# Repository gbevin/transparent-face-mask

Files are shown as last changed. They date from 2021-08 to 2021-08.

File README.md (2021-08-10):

# Transparent Reusable Face Mask

Vacuum formed and 3D printed transparent face mask with replaceable filters and an excellent seal.

I've made and donated over 1000 opaque 3D printed masks that have been fit-tested and and particle tested with great results. Using the same shape and fundamental design, I spent 4 months designing a transparent mask that fits better, has more airflow and better filtration.

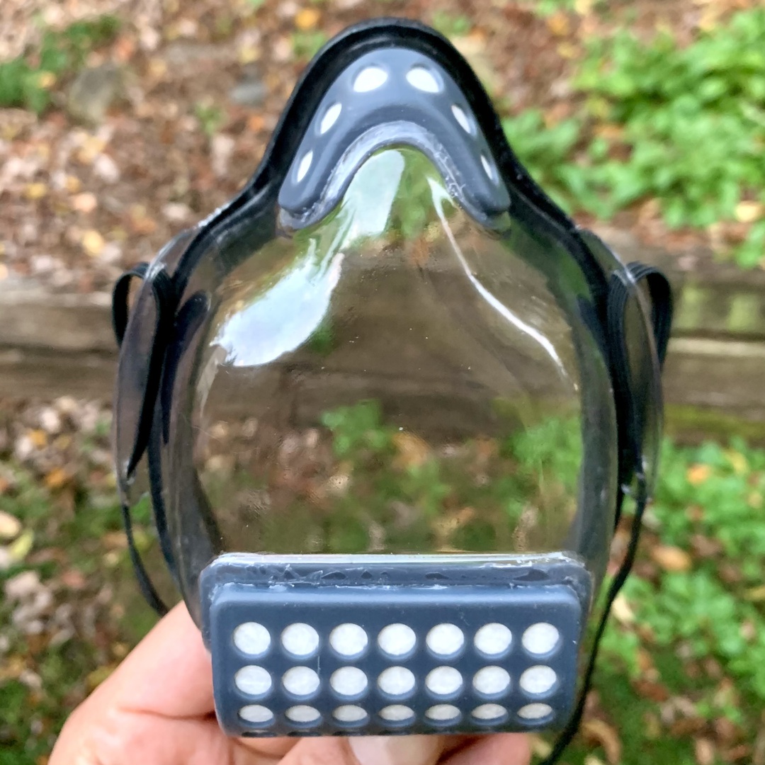
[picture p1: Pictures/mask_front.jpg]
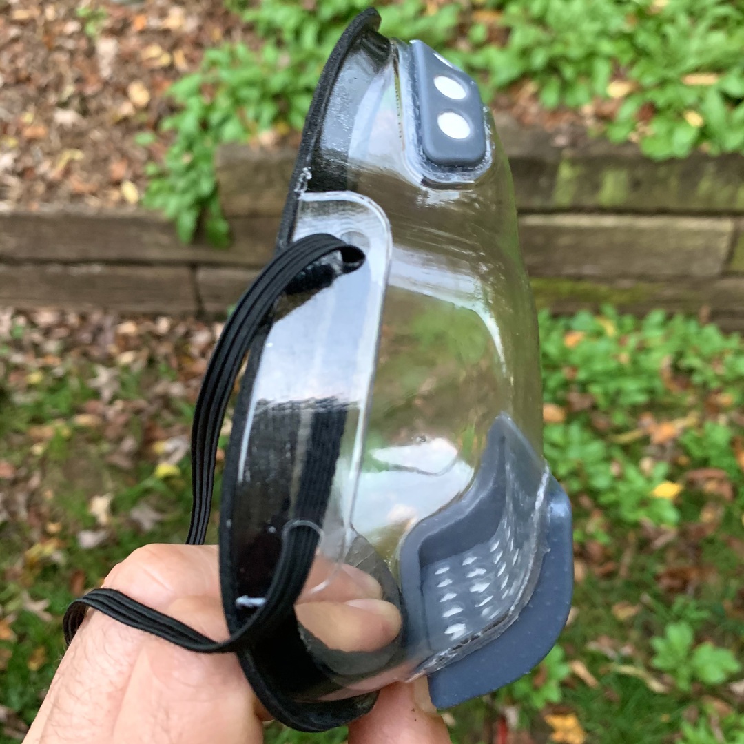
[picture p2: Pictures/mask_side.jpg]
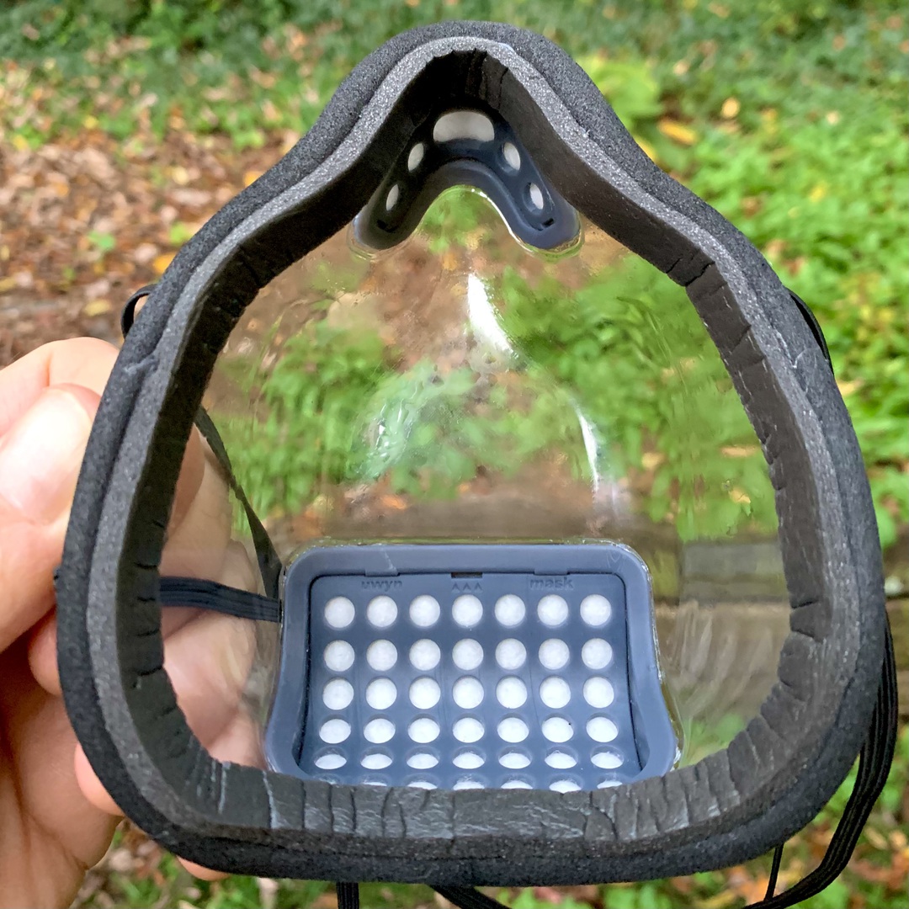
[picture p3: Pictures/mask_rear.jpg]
  

Created by Geert Bevin.

This work is freely distributed under the CC BY-SA 4.0 License.

If you want to support my efforts, please consider donating through:
http://paypal.me/geertbevin

## Design

The design was made with Moment of Inspiration: http://moi3d.com

You'll find the `3dm` files in the `Design` folder.

## Build Instructions

Detailed instructions on how to build this mask is available in the [included howto](https://htmlpreview.github.io/?https://github.com/gbevin/transparent-face-mask/blob/master/Instructions/howto.html).

## Features

* works with FaceID, might require setup of alternate appearance
* excellent smile and lip-reading visibility
* great airflow through natural vertical convection (top and bottom openings)
* replaceable filters that can be cut from any flat filter material (shape templates included)
* can be treated with temporary anti-fog spray
* edge is lined with soft weather-sealing foam to create an excellent seal
* flexible but rigid mask shell allows for comfortable facial muscle movements

## Sizing

For masks sizing: measure down from the bridge of the nose to the bottom of the chin. Don't follow the curve, make sure to measure in a straight line, see photo.

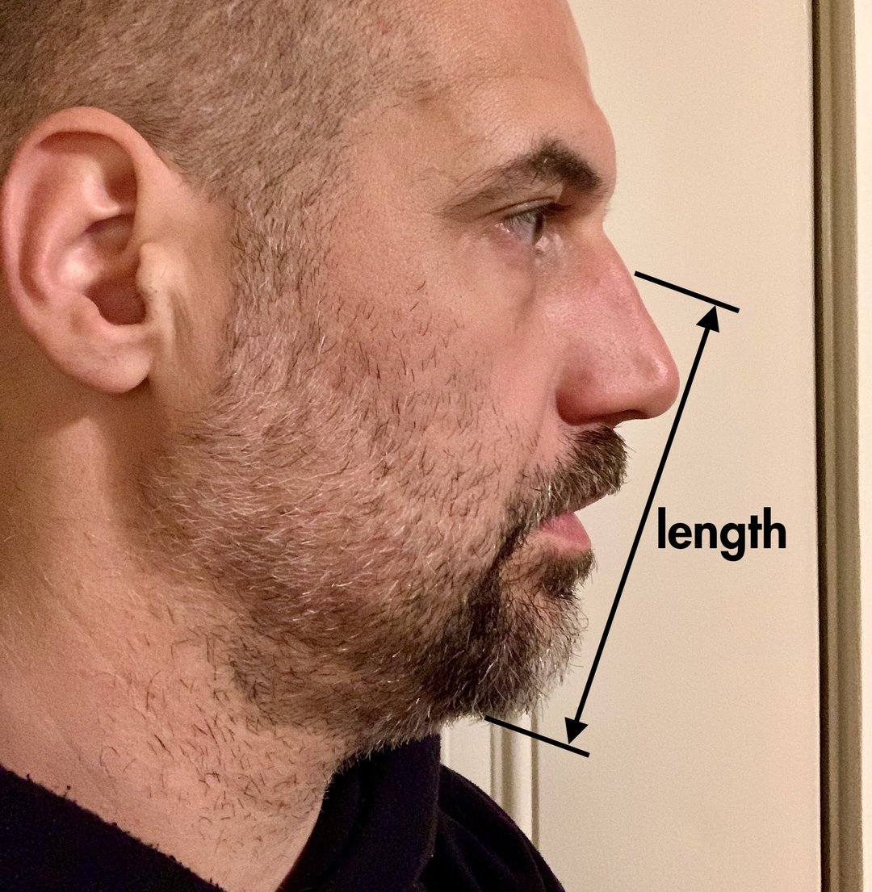
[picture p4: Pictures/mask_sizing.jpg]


This is how the sizes relate to the measured length:
* XL : length >= 5"
* L : length 4.5"-5"
* M : length < 4.5"

## Filters

It's recommended to daily replace the filters when in constant use.
For occasional use, weekly replacement is acceptable.

Recommended filter materials are:
* Filti : https://filti.com/product/filti-face-mask-material/
* BioDefensor: https://biodefensor.com

## Anti-fog

Anti-fog spray should be applied by using a microfibre cloth, spraying the cloth in order to not wet the mask's filters, then gently pat (not wipe) the inside of the mask with the humidified part of the cloth. Let dry overnight.

Recommended anti-fog products:
* Rain-X : https://www.rainx.com/product/glass-water-repellents-cleaners/rainx-anti-fog

Outside use of the mask in cold temperatures will cause condensation and reduced transparency.

## Disclaimer

**NO GUARANTEES:** This mask is not approved as N95 replacements and is not guaranteed to help against COVID-19 or any other disease. I have however done extensive research and the model I provide is the best I can create with my available tools and supplies.

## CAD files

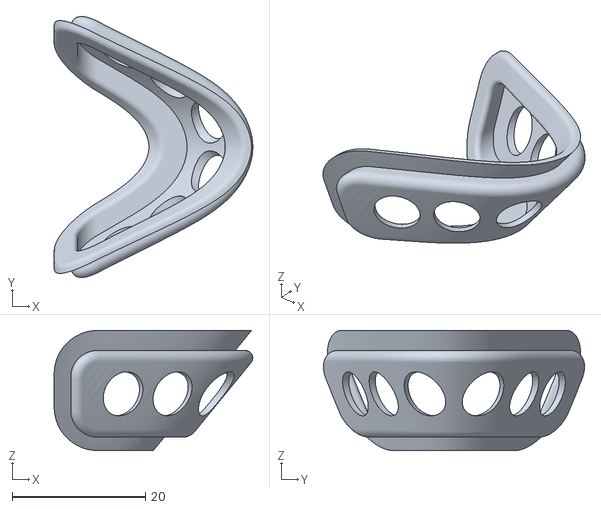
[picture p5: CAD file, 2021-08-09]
STL/large_top_insert.stl
29.8 x 39.1 x 18.0

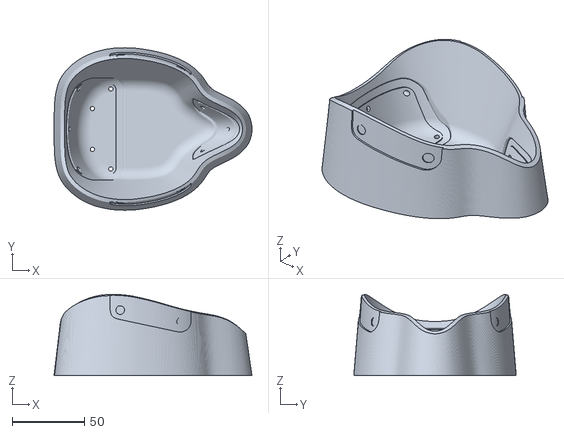
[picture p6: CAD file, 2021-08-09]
STL/large_shell_mold.stl
137.4 x 112.8 x 56.4

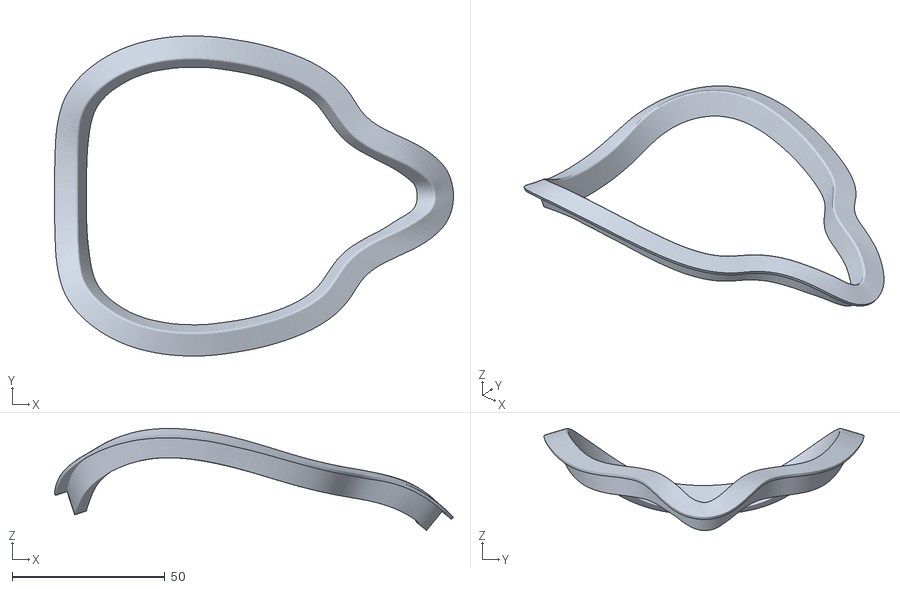
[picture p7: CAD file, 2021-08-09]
STL/large_seal.stl
130.7 x 104.8 x 33.4

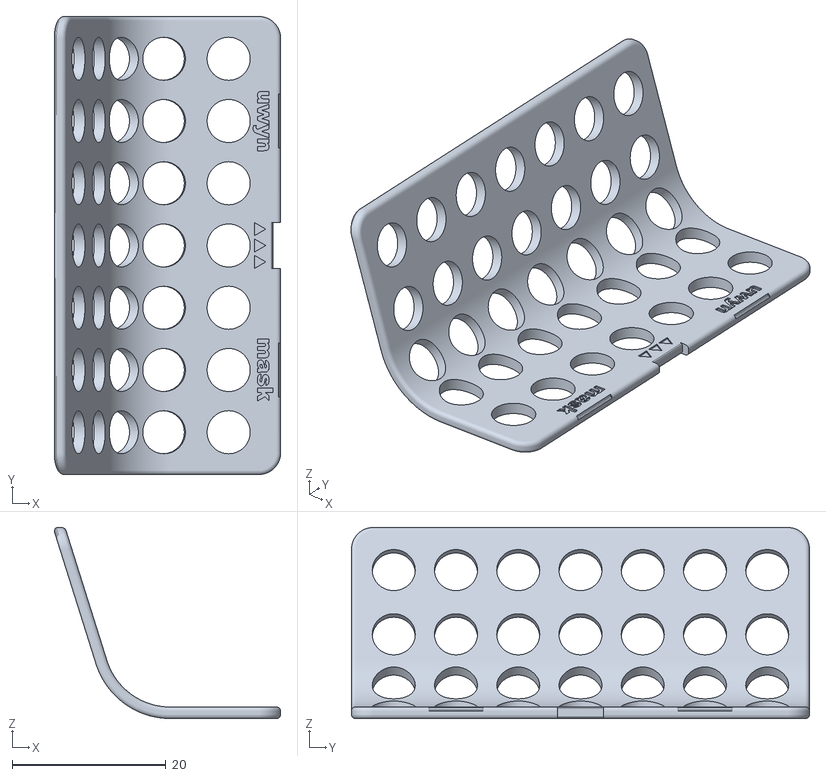
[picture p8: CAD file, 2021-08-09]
STL/medium_bottom_grate.stl
29.5 x 59.6 x 24.9

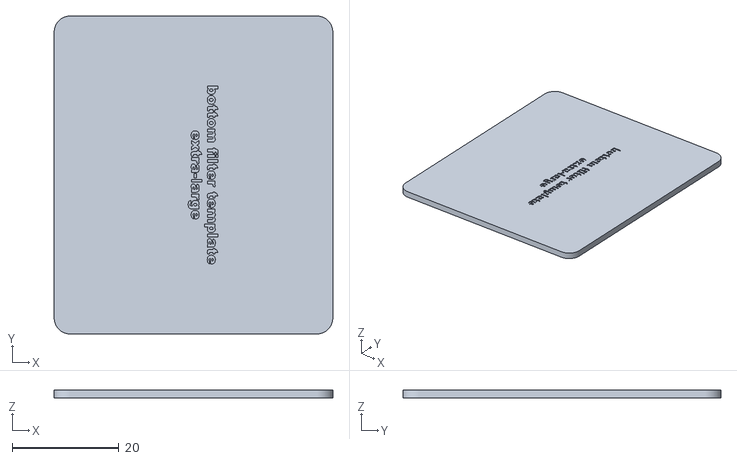
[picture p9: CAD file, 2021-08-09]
STL/extralarge_template_bottom.stl
52.2 x 59.6 x 1.50

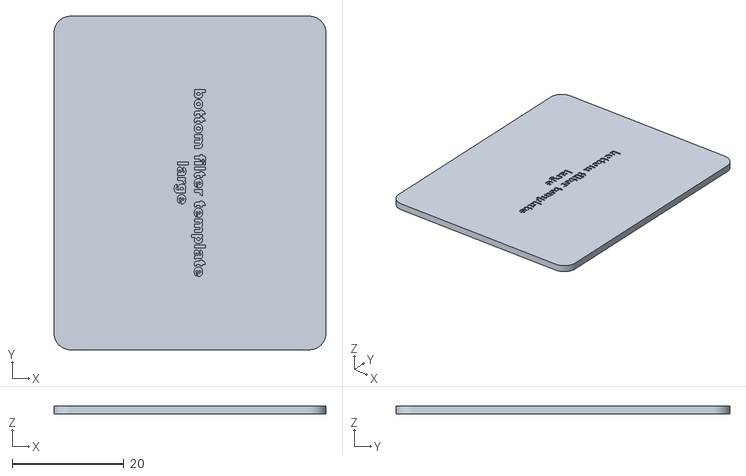
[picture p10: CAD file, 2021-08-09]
STL/large_template_bottom.stl
48.6 x 59.6 x 1.50

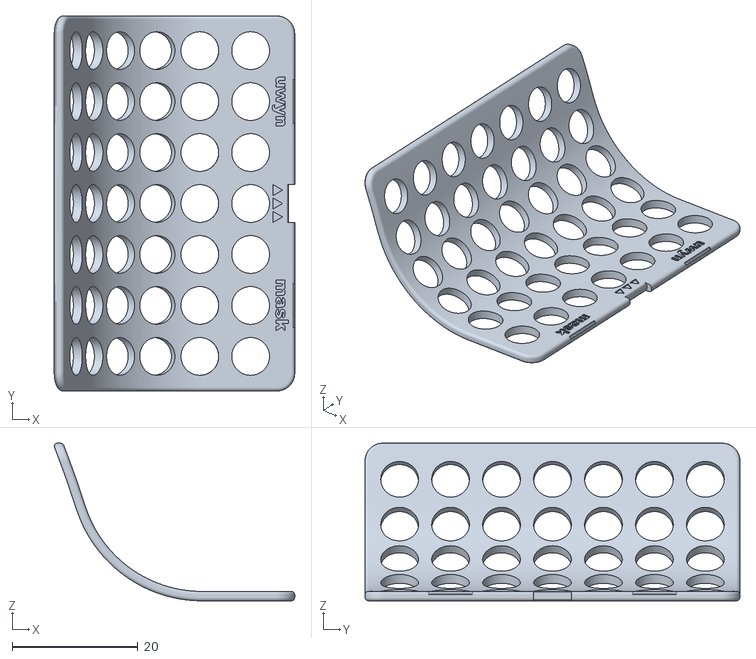
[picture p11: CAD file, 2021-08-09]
STL/extralarge_bottom_grate.stl
38.2 x 59.6 x 25.1

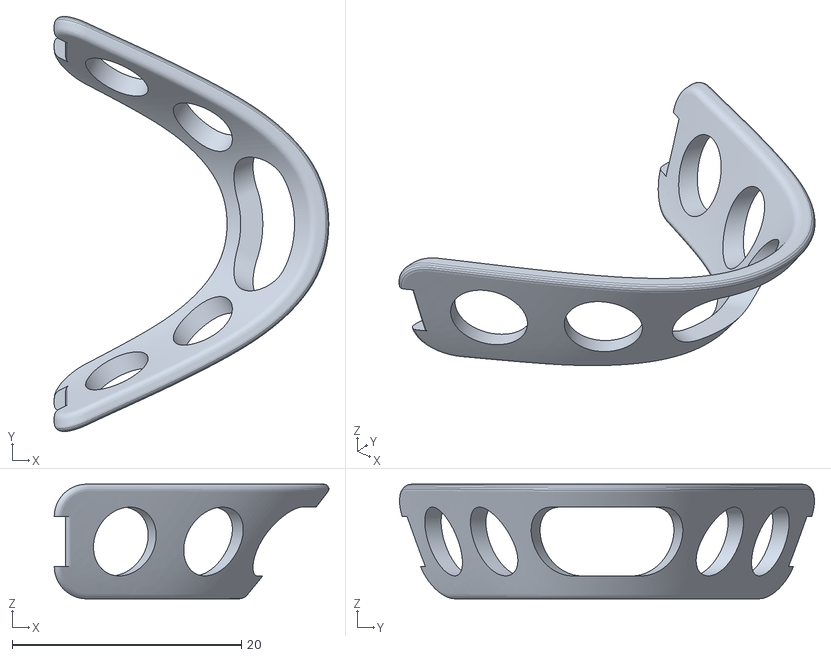
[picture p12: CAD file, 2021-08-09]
STL/extralarge_top_grate.stl
24.0 x 36.2 x 10.0

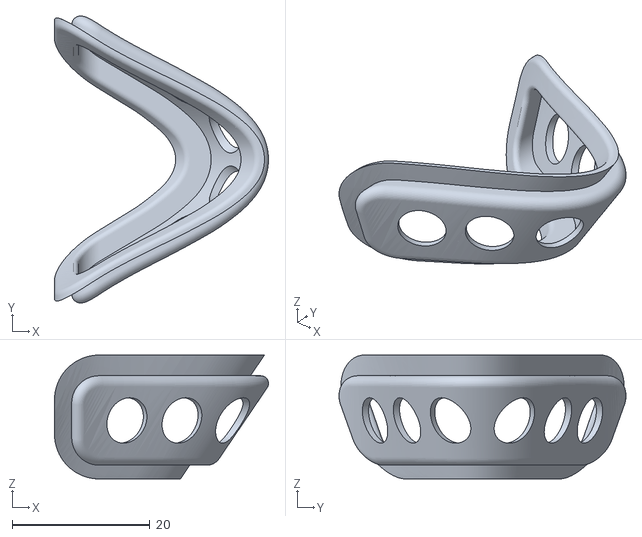
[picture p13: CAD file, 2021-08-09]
STL/medium_top_insert.stl
31.1 x 41.7 x 18.0

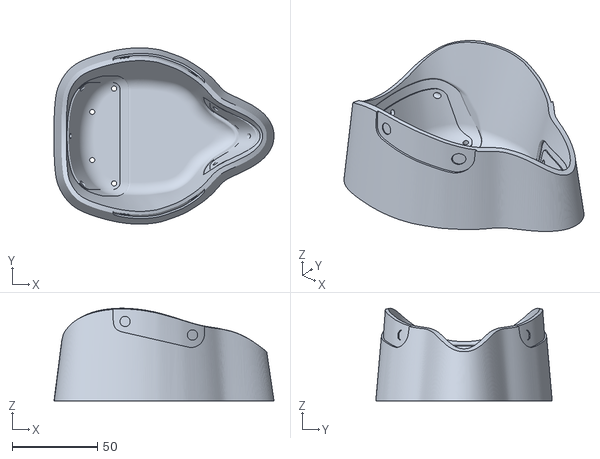
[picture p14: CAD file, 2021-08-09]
STL/medium_shell_mold.stl
129.1 x 103.5 x 54.3

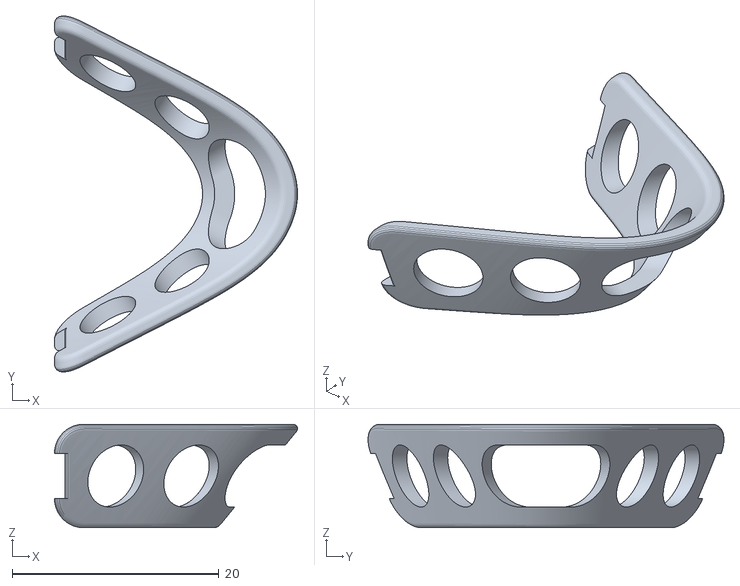
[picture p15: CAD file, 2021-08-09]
STL/large_top_grate.stl
23.5 x 34.4 x 10.0

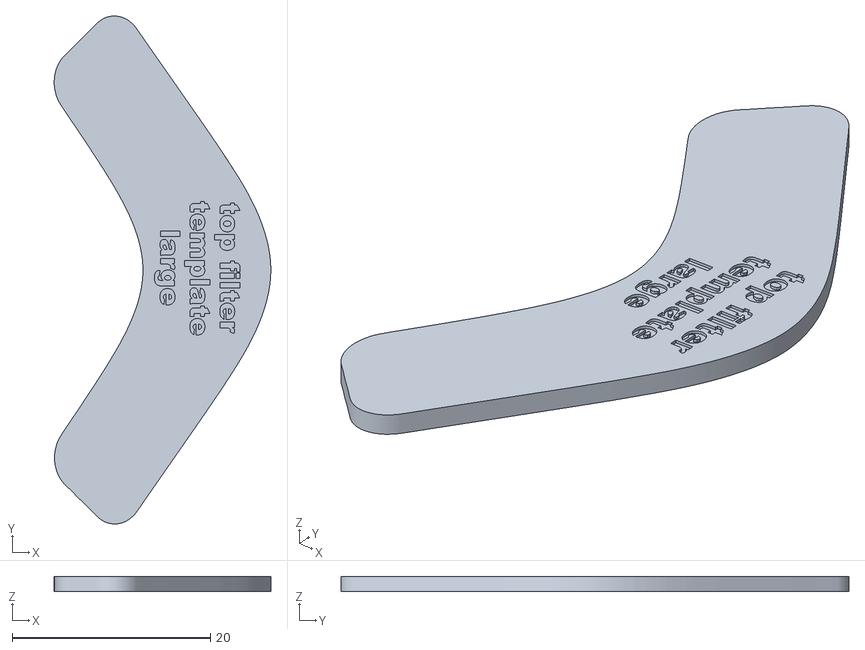
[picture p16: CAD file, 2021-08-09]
STL/large_template_top.stl
21.9 x 51.3 x 1.50

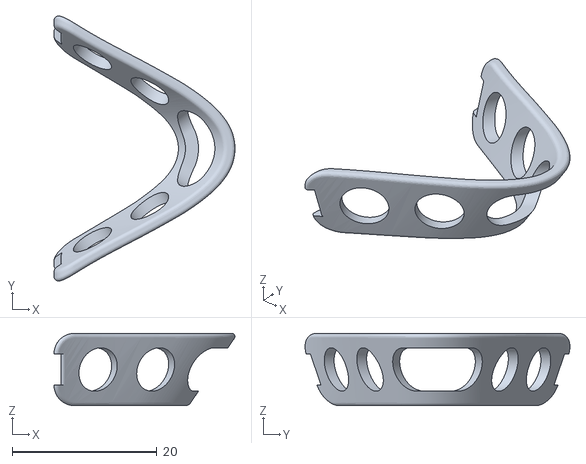
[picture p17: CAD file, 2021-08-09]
STL/medium_top_grate.stl
25.0 x 36.6 x 10.0

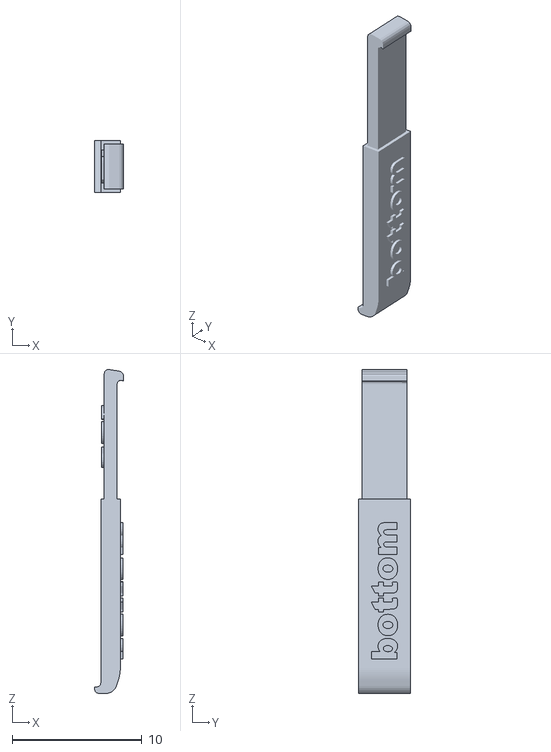
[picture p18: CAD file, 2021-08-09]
STL/large_grate_pull.stl
2.25 x 4.00 x 25.0

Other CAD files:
STL/medium_bottom_insert.stl
STL/extralarge_grate_pull.stl
STL/extralarge_seal.stl
STL/large_bottom_insert.stl
STL/extralarge_bottom_insert.stl
STL/extralarge_template_top.stl
STL/extralarge_top_insert.stl
STL/large_bottom_grate.stl
STL/medium_grate_pull.stl
STL/medium_seal.stl
STL/medium_template_bottom.stl
STL/medium_template_top.stl

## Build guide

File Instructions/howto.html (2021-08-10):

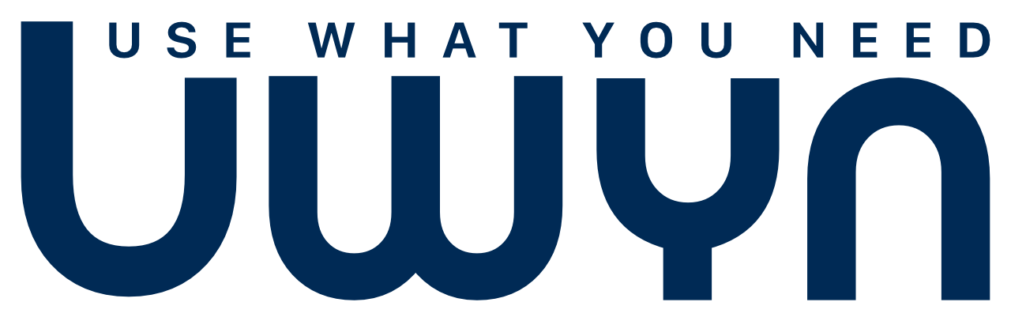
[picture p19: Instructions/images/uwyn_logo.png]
Uwyn logo
 (http://uwyn.com)

Transparent Reusable Face Mask
Build Instructions

# Introduction

During the 2020 COVID-19 pandemic, I have made and donated over 1000 opaque 3D printed masks that have been fit-tested and particle tested with great results. Using the same basic shape and fundamental design, I spent four months designing a transparent mask that fits better, has more airflow and better filtration.

  

## Feature Overview

- works with FaceID, might require setup of alternate appearance
- excellent smile and lip-reading visibility
- great airflow through natural vertical convection (top and bottom openings)
- replaceable filters that can be cut from any flat filter material (shape templates included)
- can be treated with temporary anti-fog spray
- edge is lined with soft weather-sealing foam to create an excellent seal
- flexible but rigid mask shell allows for comfortable facial muscle movements

NO GUARANTEES: This mask is not approved as N95 replacement and is not guaranteed to help against COVID-19 or any other disease.

These instructions will step you through how to make these transparent masks using the tools and equipment that are at my disposal. I've provided the design files and STL exports for you to be able to adapt these instructions to your own environment.

The latest version of these files is freely available under the CC BY-SA 4.0 License from here:
https://github.com/gbevin/transparent-face-mask

# Create the Mask Mold

The shell of the mask is designed to be transparent, light, flexible, scratch and shock resistant. The most viable small scale production technology to achieve this, turned out to be vacuum forming. This heats a sheet of clear PETG plastic and pulls it over a mold by creating a vacuum. Here, this mold is 3D printed and polished in order to achieve the highest possible clarity.

The heat of vacuum forming requires molds to be heat resistant, which needs to be taken into account when selecting the 3D printing technology and material used. Having FDM and MSLA printers available, FDM with polycarbonate filament was the best choice at my disposal. For these molds, I'm using a Raise3D E2 (https://www.raise3d.com/e2/) printer and Polymaker PolyMax PC (https://us.polymaker.com/product/polymax-pc/) filament.

The print settings are:

- Nozzle: 0.4mm
- Layer: 0.1mm
- Walls: 3
- Infill: 30% Gyroid
- Extruder temperature: 270°C
- Bed temperature: 100°C

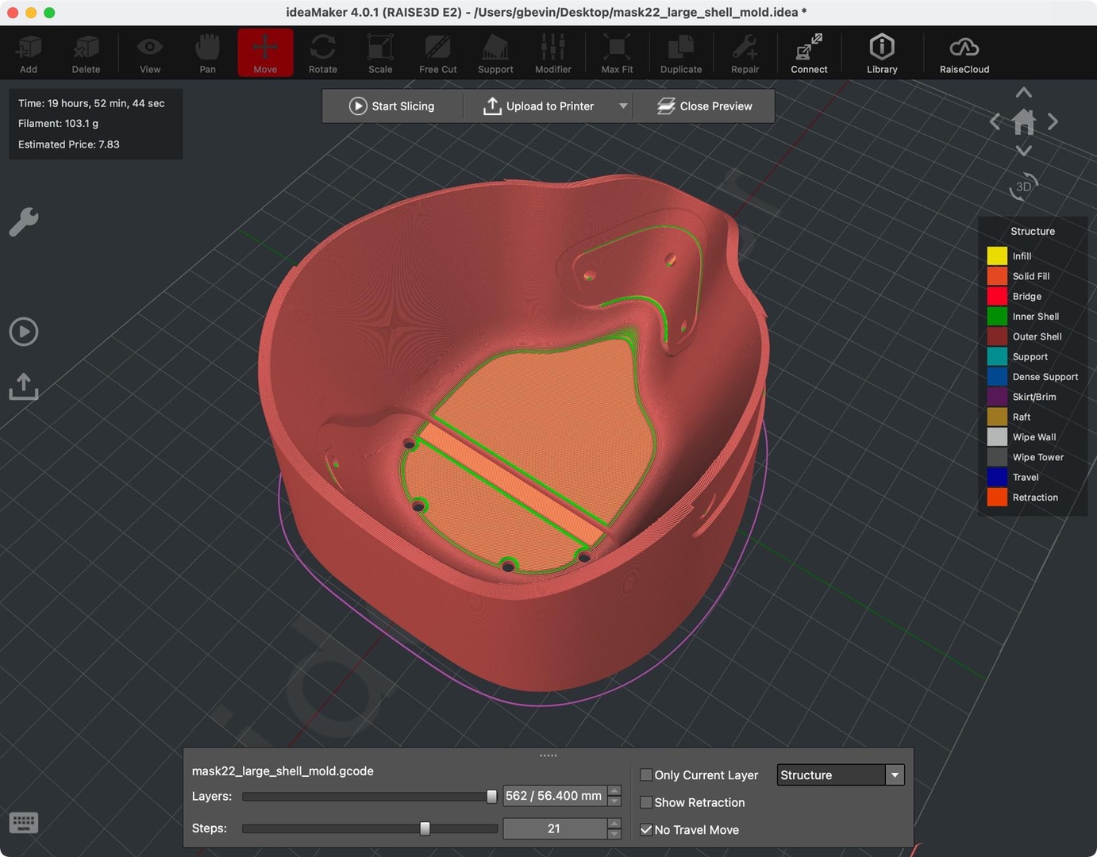
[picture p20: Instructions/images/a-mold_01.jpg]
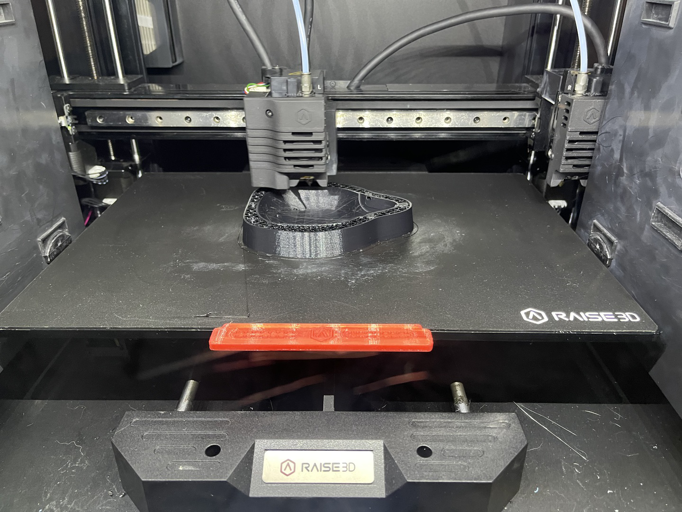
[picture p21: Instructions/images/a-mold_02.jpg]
 

Once the mold has finished printing, it's important to sand and polish it to the finest smoothness possible because vacuum forming will transfer even the smallest imperfection to the plastic that's pulled over the mold.

Finishing the mold is a very labor intensive process as you manually go through a series of sand paper grits. I'm using the following in order: 80, 150, 220, 320, 400, 800, 1000, and 3000. Don't press too hard because there is a risk of separating filament layers and creating unintended holes as they come loose during sanding. You can achieve a very smooth finish by using Brasso as the last step with a microfiber cloth.

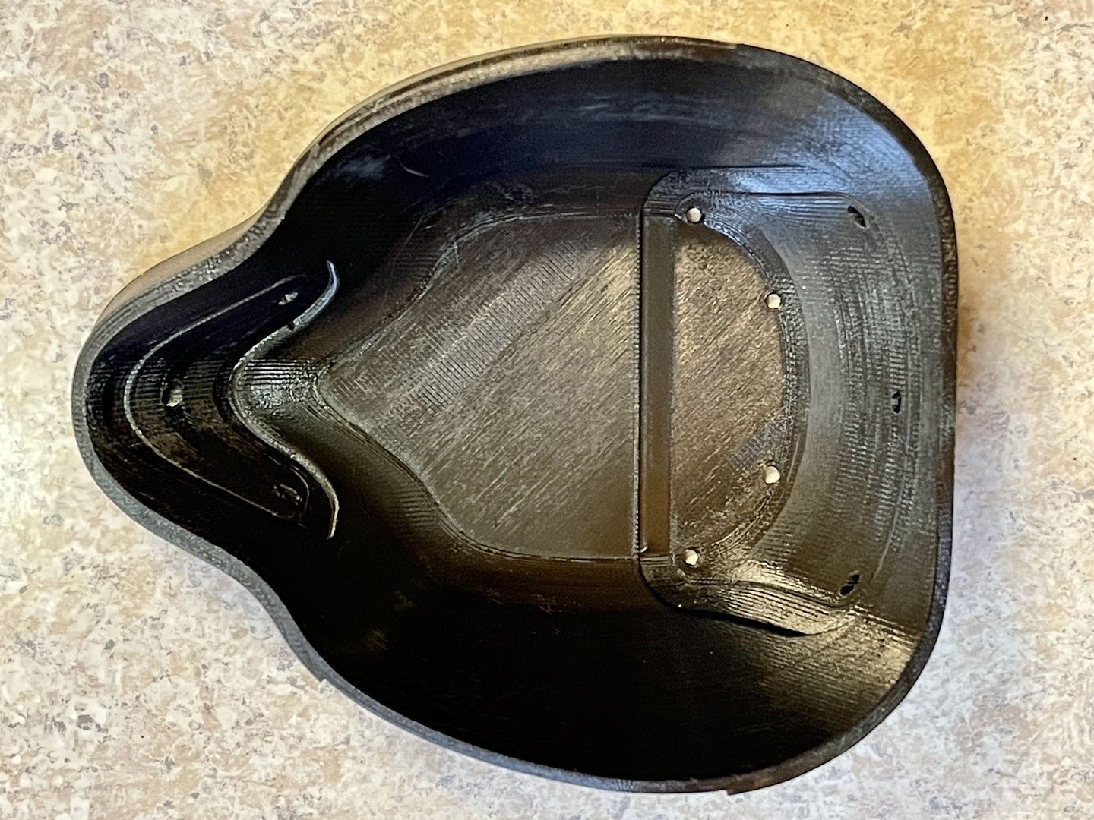
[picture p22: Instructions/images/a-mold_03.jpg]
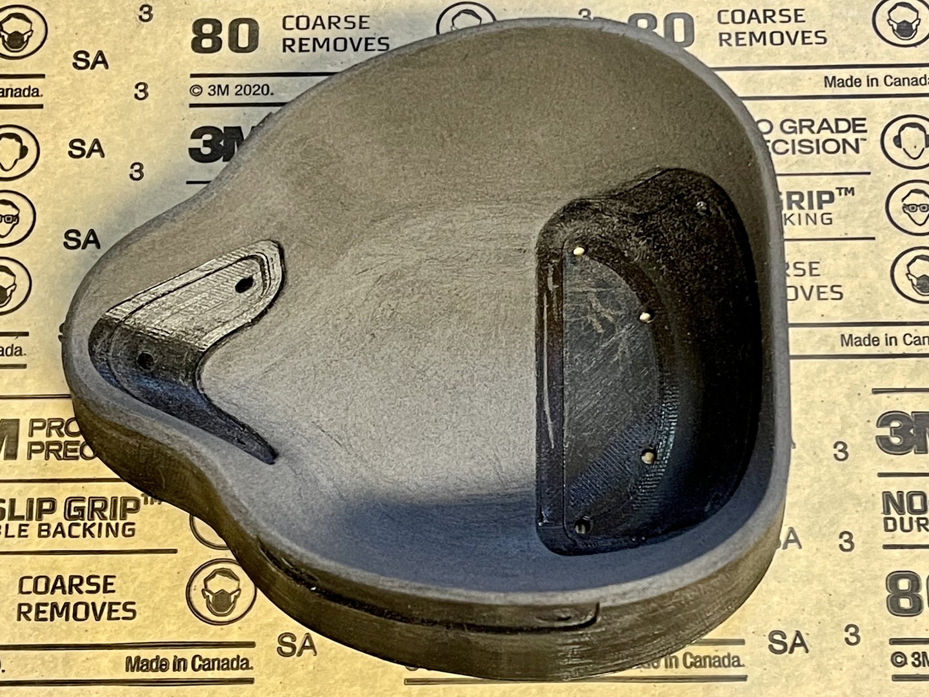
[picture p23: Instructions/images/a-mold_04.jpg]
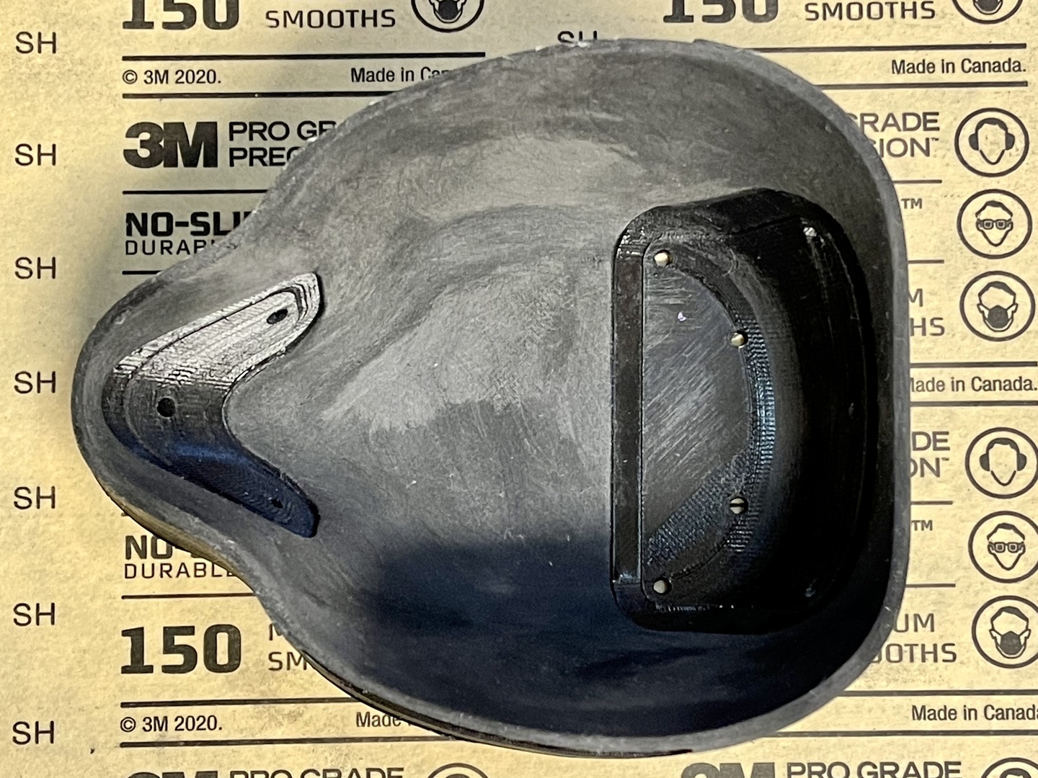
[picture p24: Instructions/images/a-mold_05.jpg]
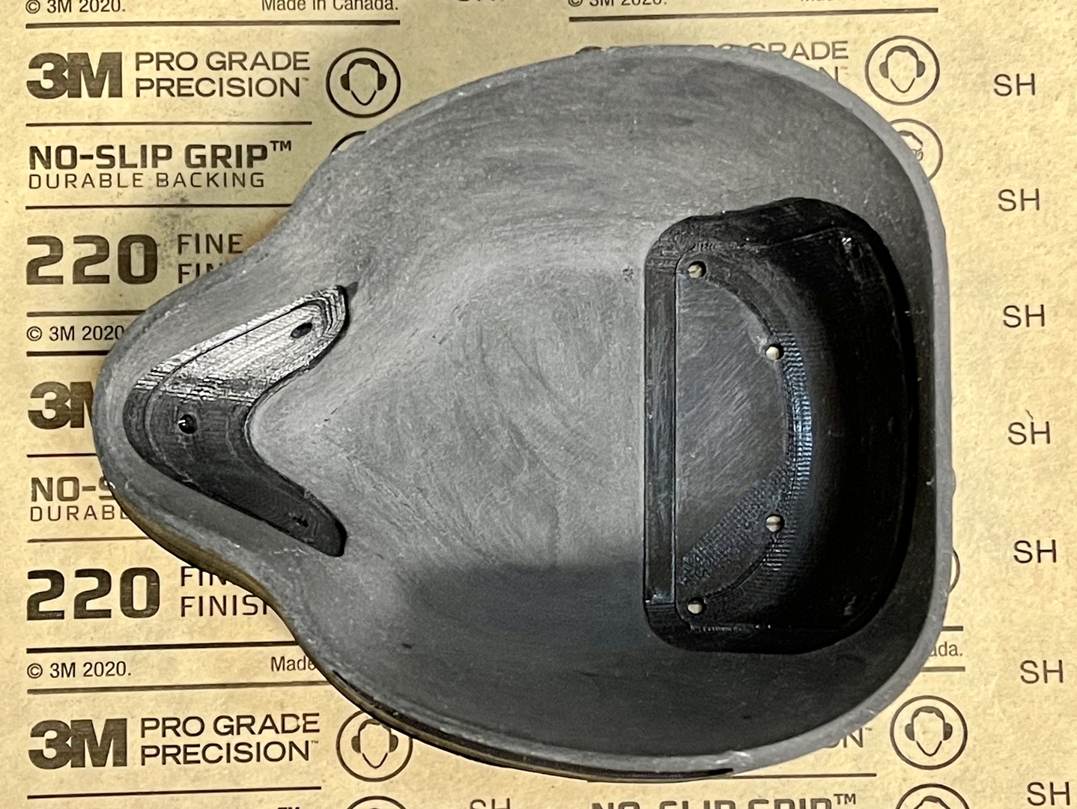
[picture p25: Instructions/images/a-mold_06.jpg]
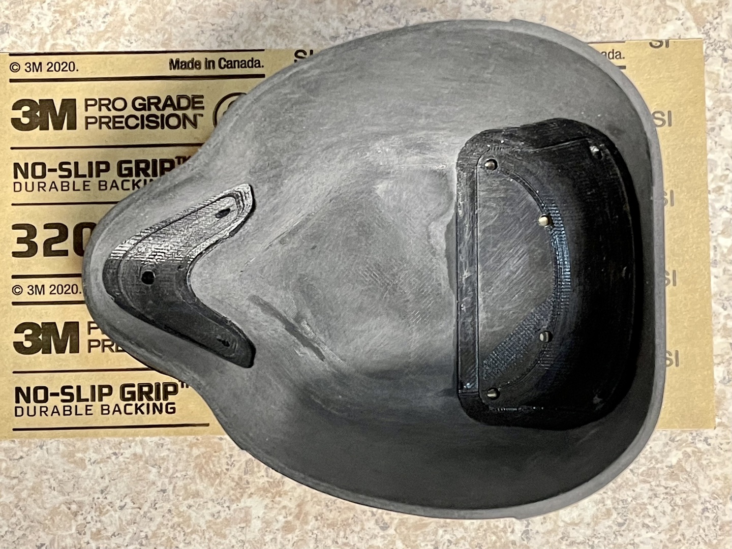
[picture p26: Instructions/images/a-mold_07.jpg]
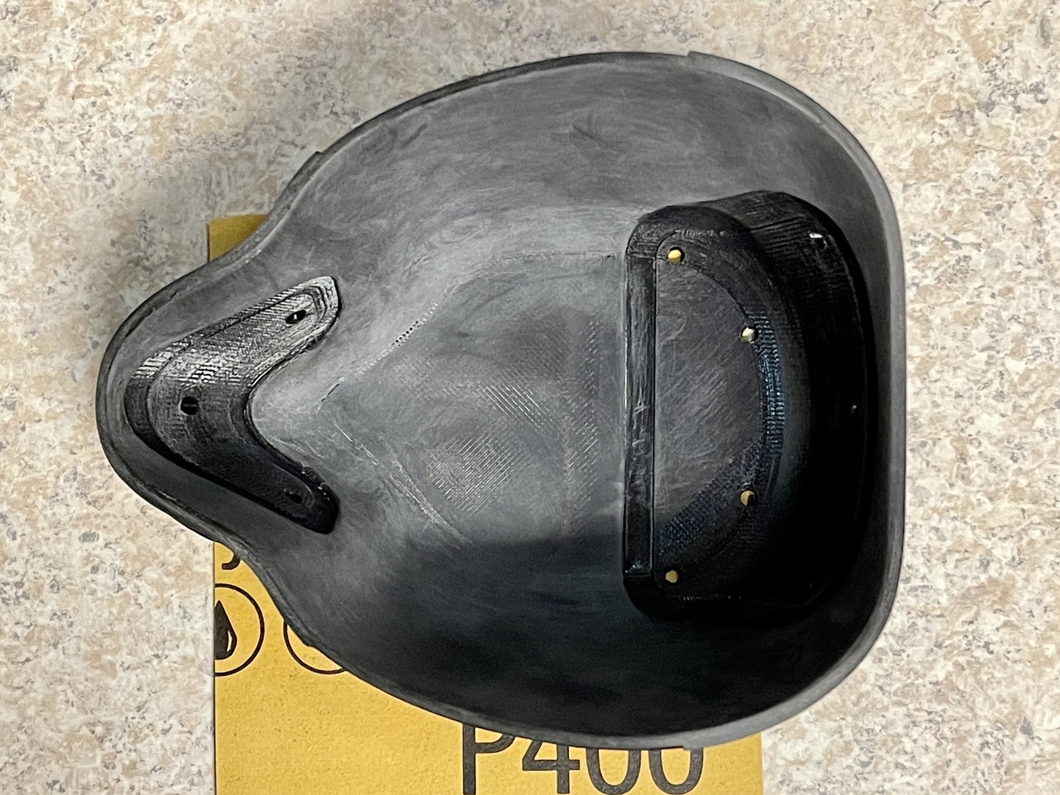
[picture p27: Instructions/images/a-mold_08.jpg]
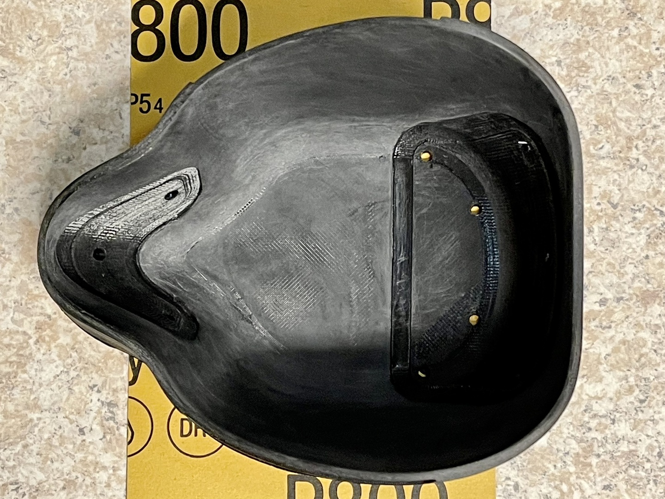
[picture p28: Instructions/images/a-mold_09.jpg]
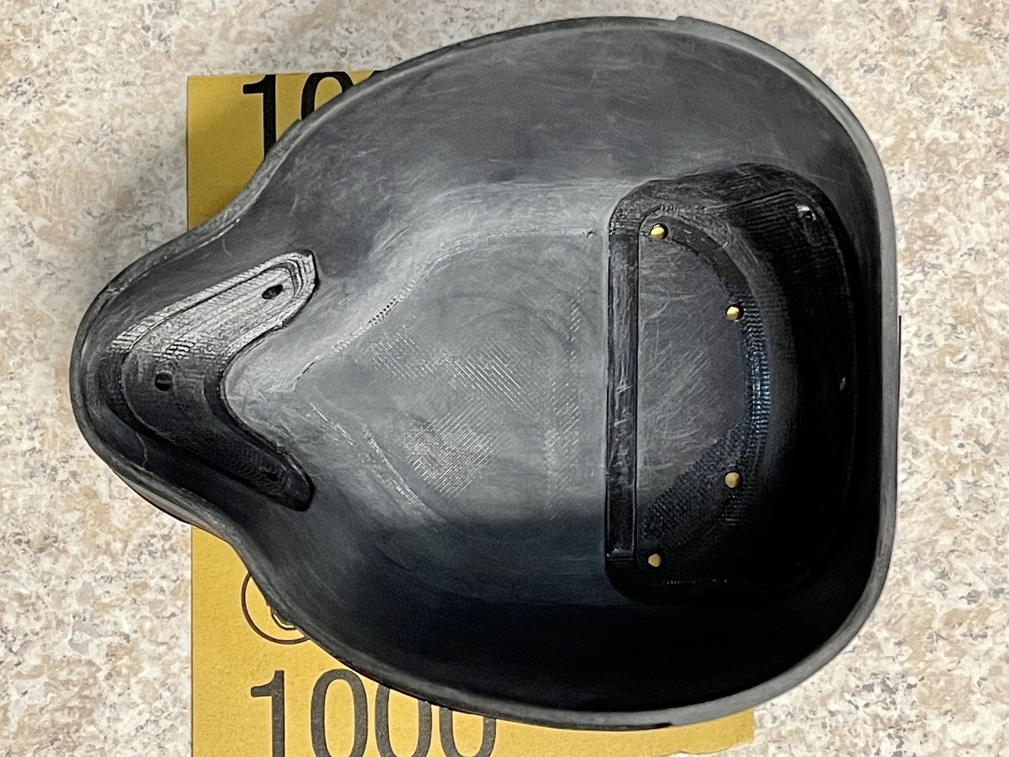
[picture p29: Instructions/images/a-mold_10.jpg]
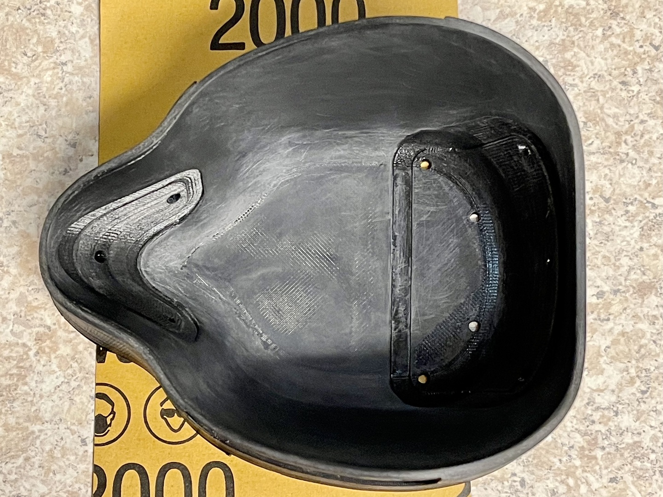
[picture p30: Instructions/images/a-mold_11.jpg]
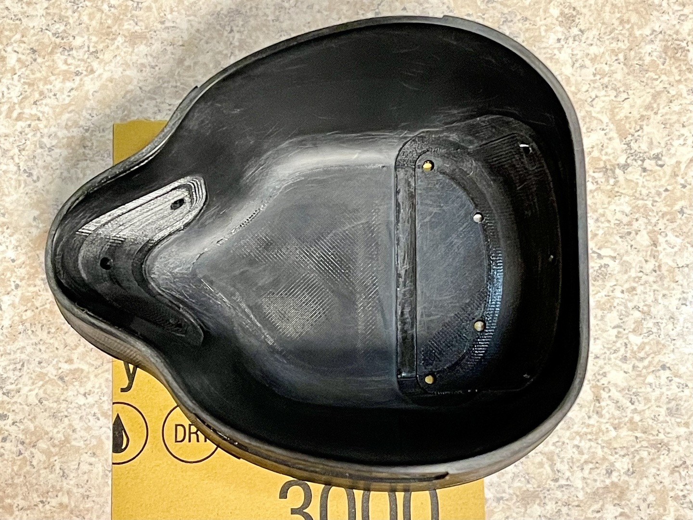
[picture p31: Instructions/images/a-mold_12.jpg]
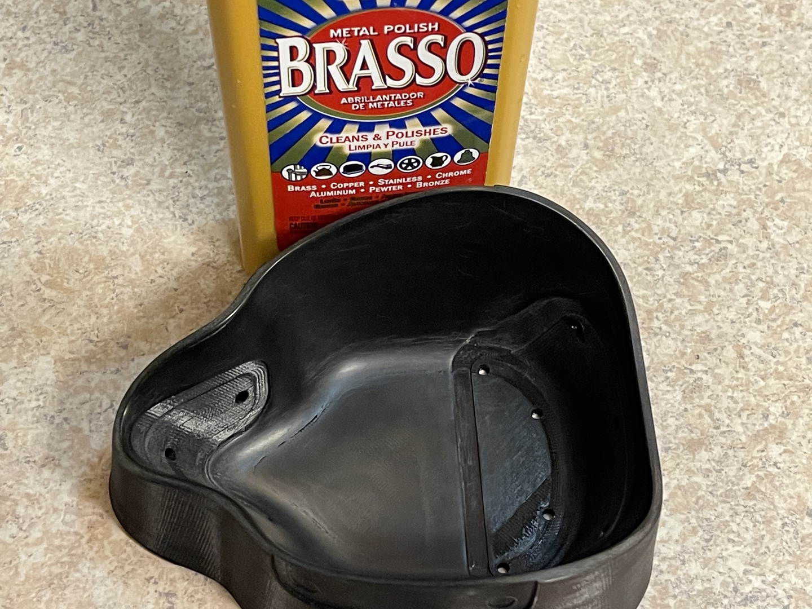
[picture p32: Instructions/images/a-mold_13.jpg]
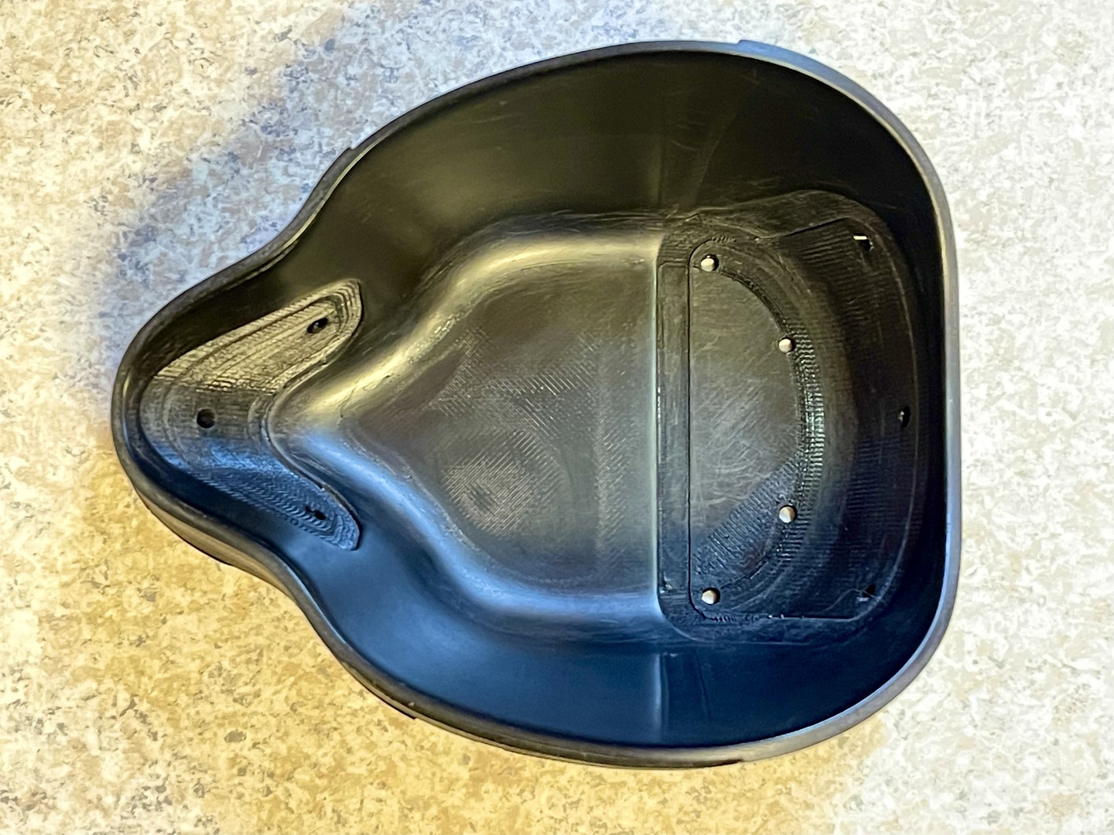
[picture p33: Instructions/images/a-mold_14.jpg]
           

# 3D Print the Mask Inserts

Inserts will be glued into the transparent shell in order to provide rigidity, to hold the replaceable filters and to prevent any air from entering or leaving the mask without having gone through filter material. These inserts can be printed with MSLA printers with minimal supports and when using a suitable resin, still provide enough strength and rigidity for daily use. I'm using an Epax3D X1K 6" Mono Printer (https://epax3d.com/collections/x-series-1/products/epax-x1k-mono-lcd-3d-printer) with the Epax3D Hard and Tough Resin (https://epax3d.com/collections/epax-resins/products/epax-abs-like-resin-gray) to which I've added additional black UV pigment (https://www.3dresinsolutions.com/products/cmykw-pigment-set) to create a darker shade of gray.

Once you've finished printing the inserts, grates, filter templates and little crowbar, remove the supports and thoroughly wash the items in 99% isopropyl alcohol. You'll have to keep your washing liquid fairly clean in order to prevent any residue from accumulating on the surfaces.

Make sure to wear appropriate PPE yourself when handling resin, especially heavy duty nitrile gloves (https://www.amazon.com/dp/B0192K9T78/ref=cm_sw_em_r_mt_dp_1HTX1VTY6T1CM7PHTT3E).

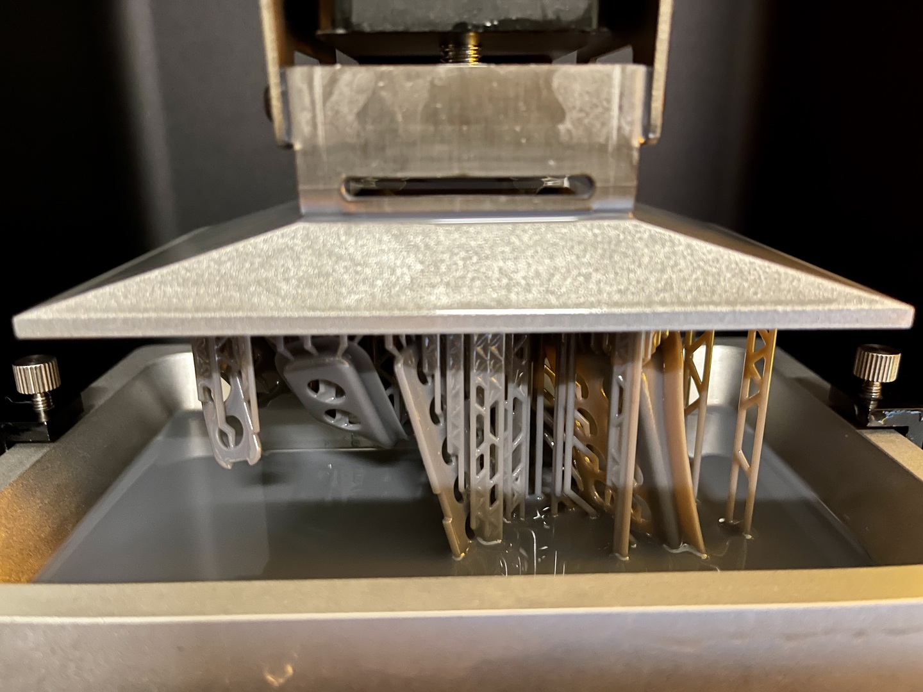
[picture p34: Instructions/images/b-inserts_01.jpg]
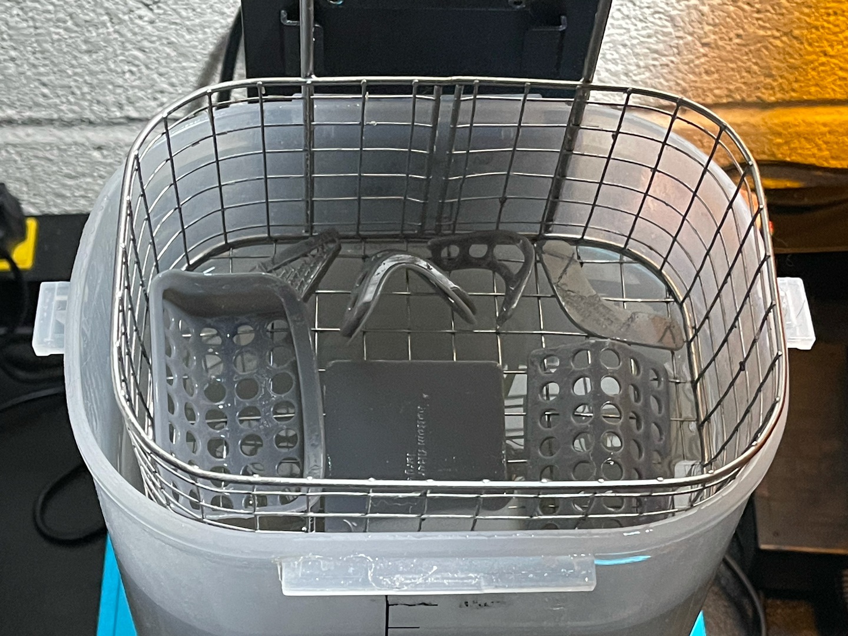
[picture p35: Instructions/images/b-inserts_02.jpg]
 

Let the items dry for at least 30 minutes when you remove them from the washing liquid. Afterwards you should finish the curing of the resin by exposing the items to a strong UV light for a sufficient amount of time. For both the washing and the curing, I use an AnyCubic Wash & Cure (https://www.anycubic.com/products/anycubic-washing-curing-machine) machine.

I cure the items in this device for at least 4 minutes, then turn the items over and put them in for another 4 minutes. Since uncured resin is toxic, you should be absolutely certain that all resin is cured.

Finally, I rinse all the items under warm water to get rid of anything that might still feel sticky. Be careful with your water temperature, because when it's too hot, it will deform the resin and your items will not fit the mask's shell anymore.

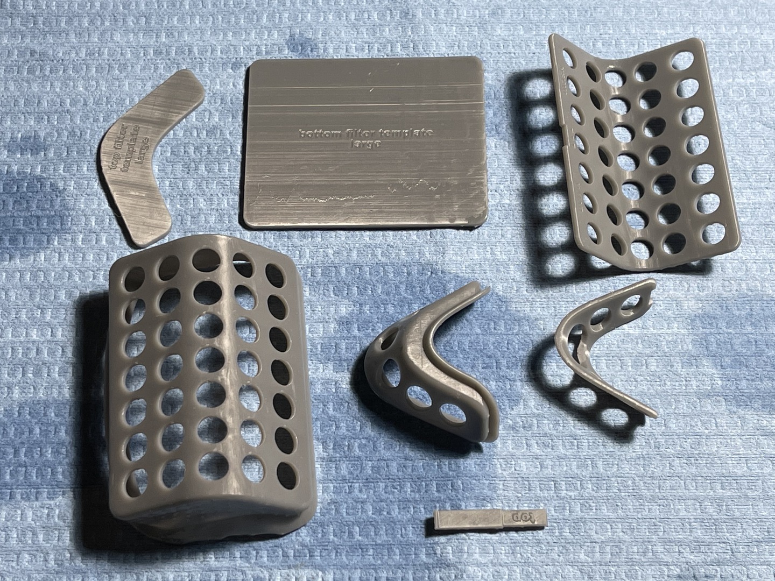
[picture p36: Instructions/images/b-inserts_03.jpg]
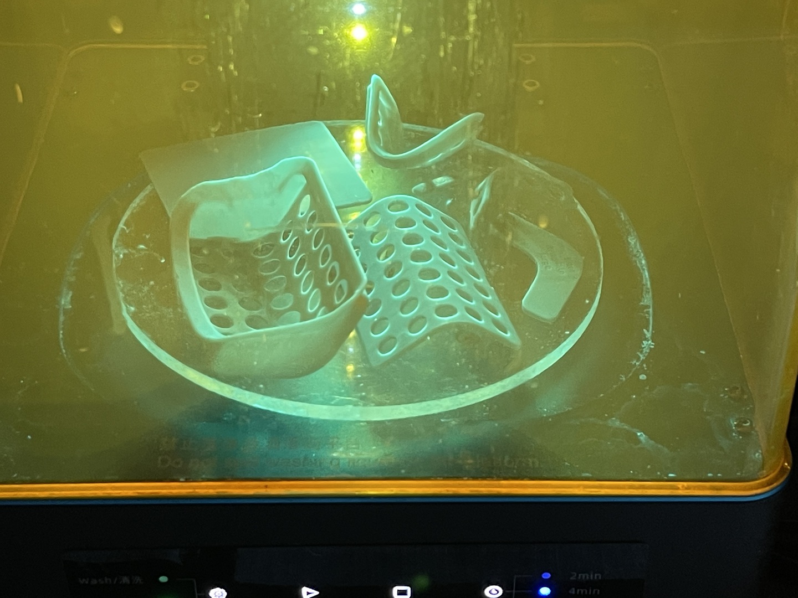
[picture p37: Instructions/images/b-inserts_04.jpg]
 

# Vacuum Form and Trim the Mask Shell

With your mold ready, you can create the transparent mask shells by vacuum forming clear PETG sheets.

I'm using a Mayku Formbox (https://www.mayku.me), which is relatively inexpensive and can be hooked up to your existing vacuum cleaner. The PETG sheets should be at least 1mm thick. A thickness of 1.5mm works also but the mask will not as easily adapt to different face shapes and mouth movements anymore due to the increased rigidity. Thinner PETG sheets become too brittle due to the large draw distance between the edges and the front of the mask. The Mayku 1mm Clear Sheets (https://www.mayku.me/products/mayku-clear-sheet-1-0mm-20-pack) work fine, but you can also order cheaper 0.040" Vivak PETG sheets from many plastic suppliers and have them cut into 9 1/4" x 9 1/4" squares, for instance from Curbell Plastics (https://www.curbellplastics.com/Shop-Materials/Product/PETG-Sheet/W01-03360/PETG-Sheet-Clear-(0-040-in-x-48-in-x-96-in)-FDA-Compliant-Film-2-sides).

Before using your mold for vacuum forming, you should apply a suitable release agent to it. The first time this might leave residue on the PETG plastic, but it will allow your mask shells to come loose without damaging the mold. I've had good results with the APEL Silicone Mold Release Spray (https://www.amazon.com/dp/B085CBSS5Y/ref=cm_sw_em_r_mt_dp_XAPEQV2G14PQ3W8JHZ4G).

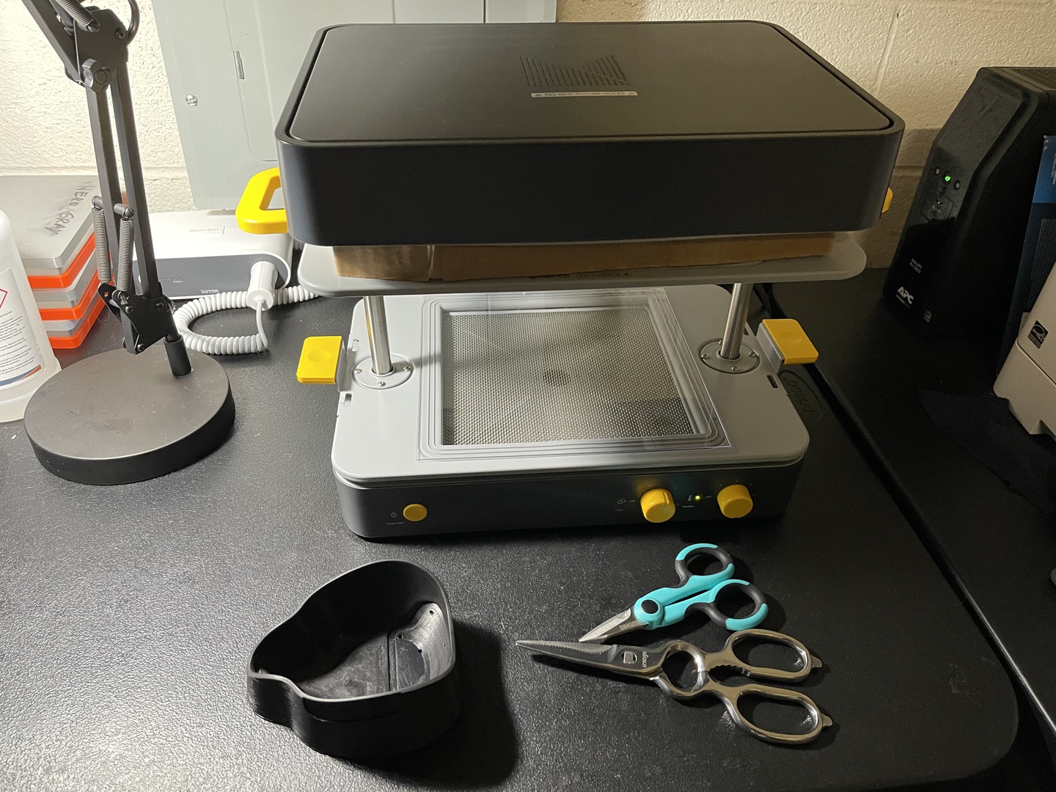
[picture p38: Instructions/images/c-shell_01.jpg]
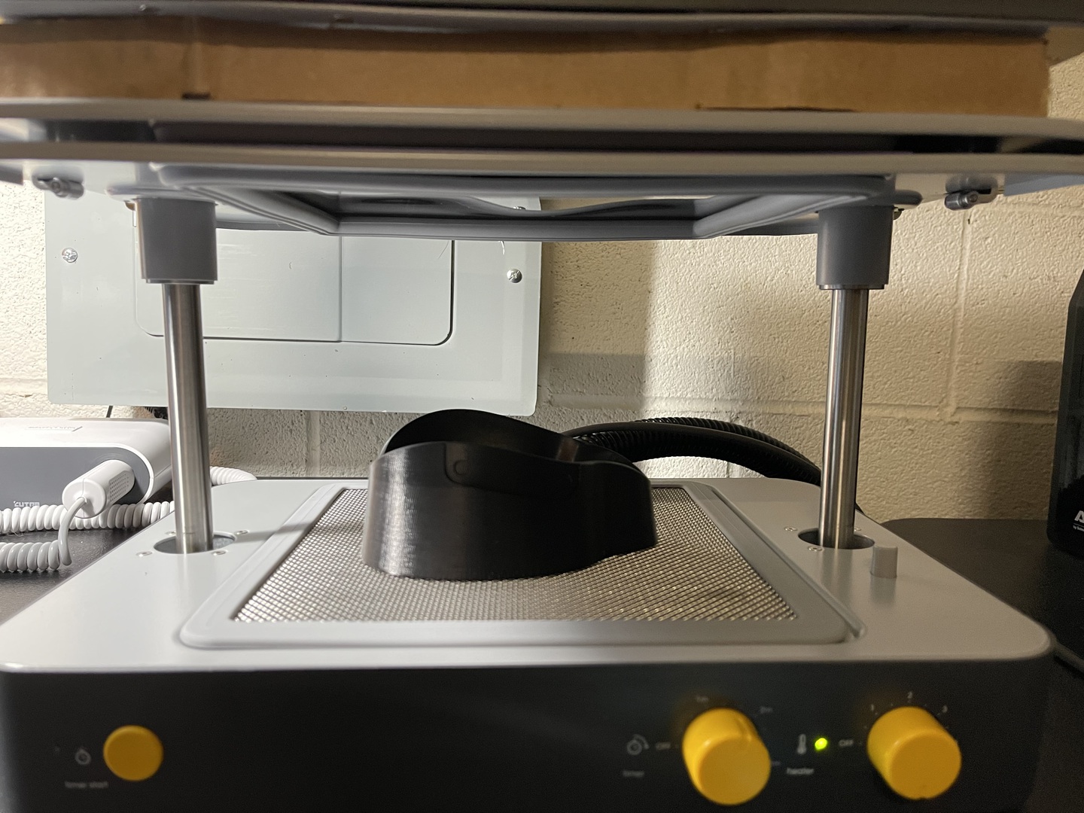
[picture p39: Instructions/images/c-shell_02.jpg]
 

Place your plastic sheet in the vacuum former and set it to the appropriate temperature and duration for your material. I set the Formbox to a temperature of 6 for 1.7 minutes. You'll notice when your sheet is warm enough when is creates a nice bell-shaped curve in the middle.

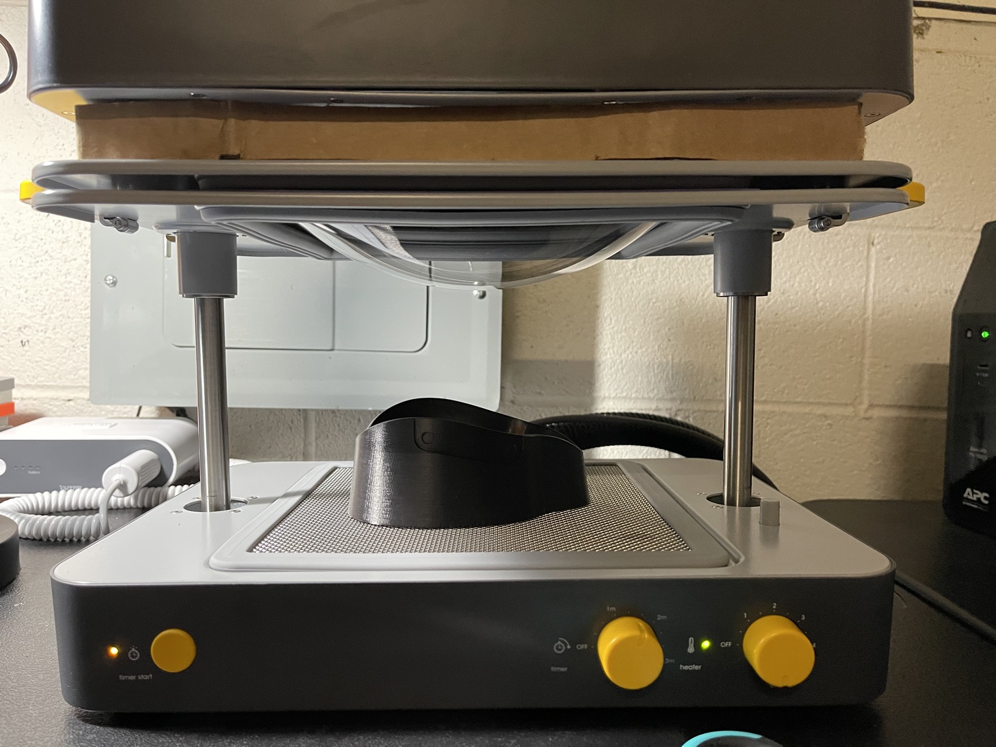
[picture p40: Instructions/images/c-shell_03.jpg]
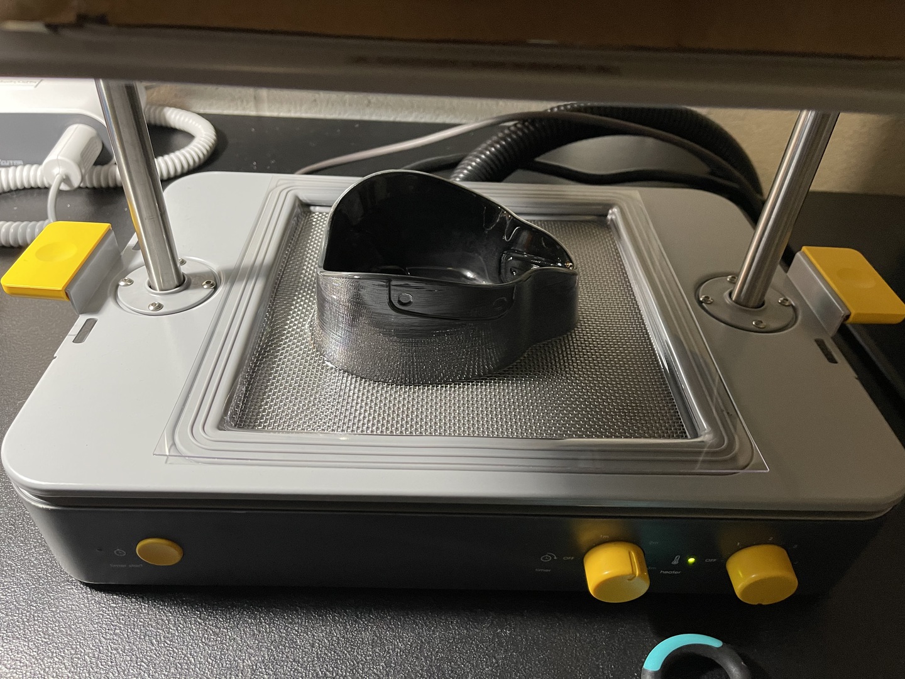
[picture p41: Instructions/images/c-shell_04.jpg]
 

Once your plastic is formed to the mold, wait a few seconds to ensure the plastic has regained some of its rigidity, otherwise you might burn yourself and deform the result by manipulating it too soon. You can roughly cut away the edges around the mask shell so that it's easier to manipulate for the next steps.

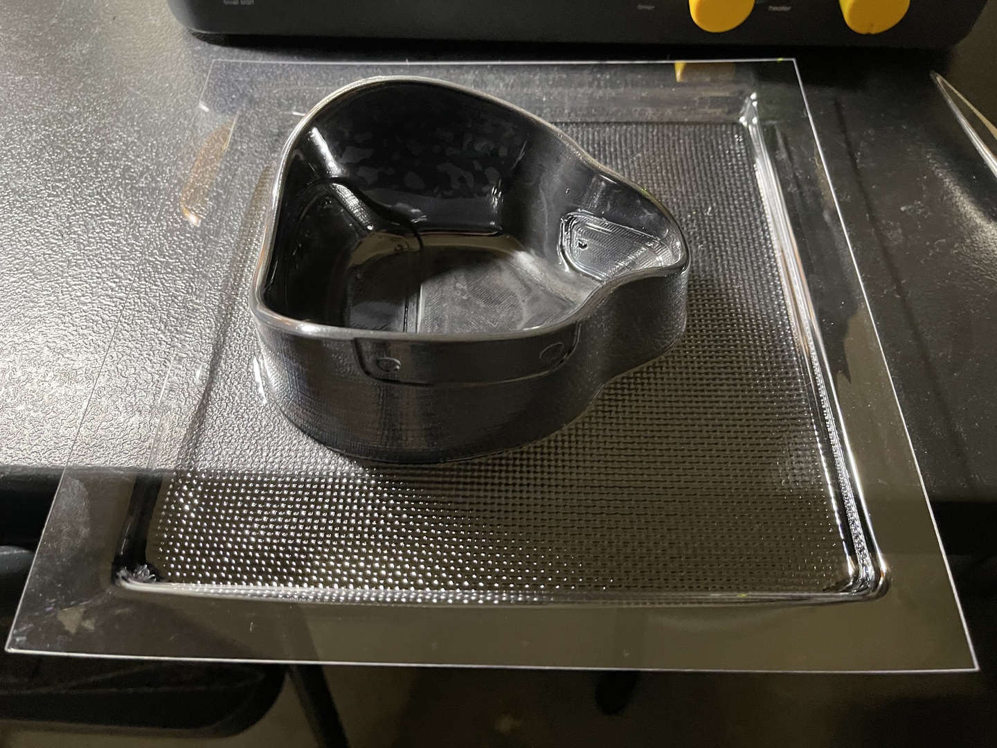
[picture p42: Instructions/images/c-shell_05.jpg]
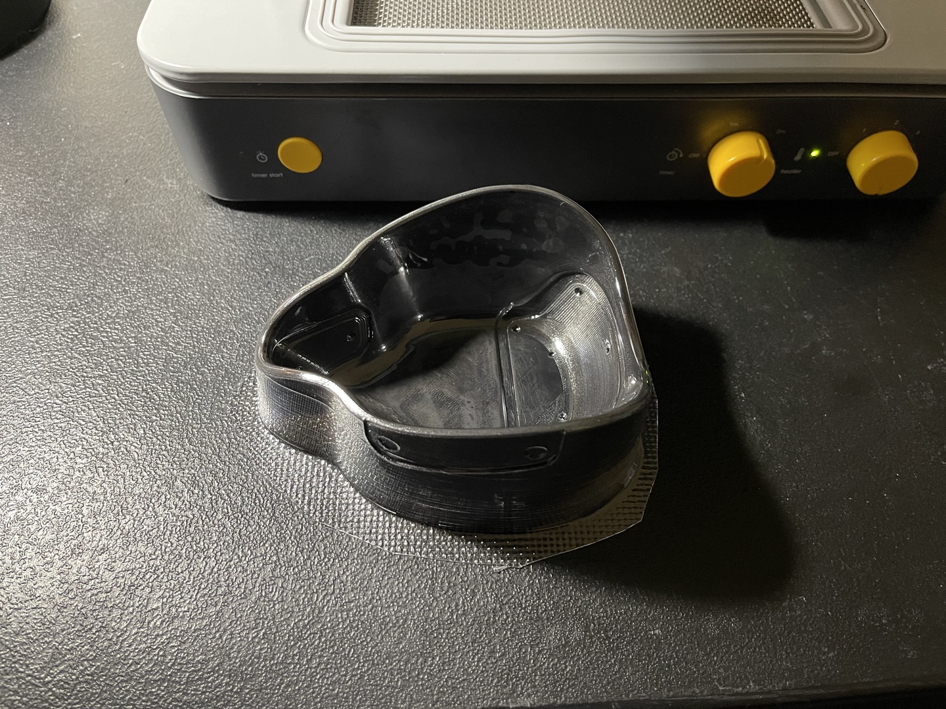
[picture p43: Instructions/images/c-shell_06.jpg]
 

Next is one of the most tedious steps of the mask build process. Using a variety of tools, you should cut along the outside edge of the mask shell without creating any jagged incisions. This part of the mask will be the closest to your face, so it's recommended for the cuts to be as clean as possible. When you've cleanly cut along the edge, you should cut out the holes in which the mask inserts will be glued. Once more, you should be very precise because any deviation of the shape that's indicated by the mold, will not provide enough support for the mask inserts to naturally hold in place. Finally, don't forget to create holes in the side flaps for the straps to go through.

I use a combination of tools and developed a technique that works for me. I recommend you practice and experiment on a few mask shells for a while.

These are are the tools I use:

- LIVINGO Kitchen Forged Shears Heavy Duty Ultra Sharp Multi-function Stainless Steel Scissors (https://www.amazon.com/dp/B0795FC36C/ref=cm_sw_em_r_mt_dp_QCY3T78ERVX0SGZQRBWV)
- SINGER 00558 5-1/2-Inch ProSeries Heavy Duty Scissors with Power Notch (https://www.amazon.com/dp/B00114QC9W/ref=cm_sw_em_r_mt_dp_6G68T132NJ5TK40CAFXP)
- CUTRA Wondercutter S (https://www.micromark.com/Wondercutter)
- AFA Tooling Deburring Tool with Blade, 10 High-Speed Steel BS1010 Rotary Burr Removal Blades (https://www.amazon.com/dp/B07RM1D6WD/ref=cm_sw_em_r_mt_dp_11AHDQ5R2X7GBPVAHV3A)
- Scalpel Sterile Blades #10 10pcs Sterile Individually Foil Wrapped, with #3 Scalpel Knife Handle (https://www.amazon.com/dp/B0871VSLDJ/ref=cm_sw_em_r_mt_dp_W73NJ4QZVXKKMBNTRXSB)
- KUCAA Metal Silver Hand-held 1/4 inch 6mm Round Heavy Duty Single Circle Hole Punch (https://www.amazon.com/dp/B07F27WJTK/ref=cm_sw_em_r_mt_dp_DNT9B2BDNV84N4JQRE9S)

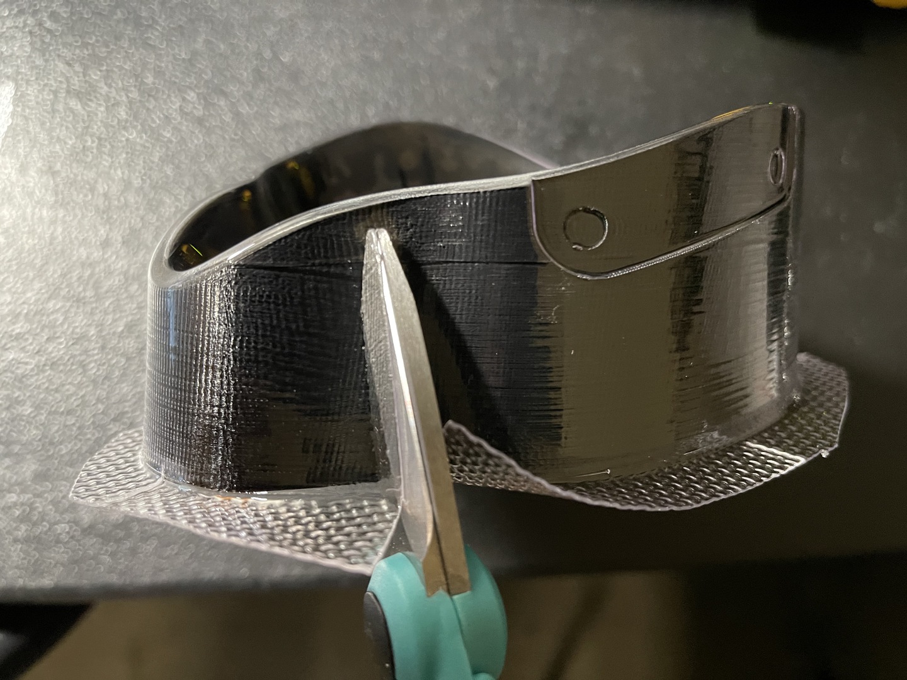
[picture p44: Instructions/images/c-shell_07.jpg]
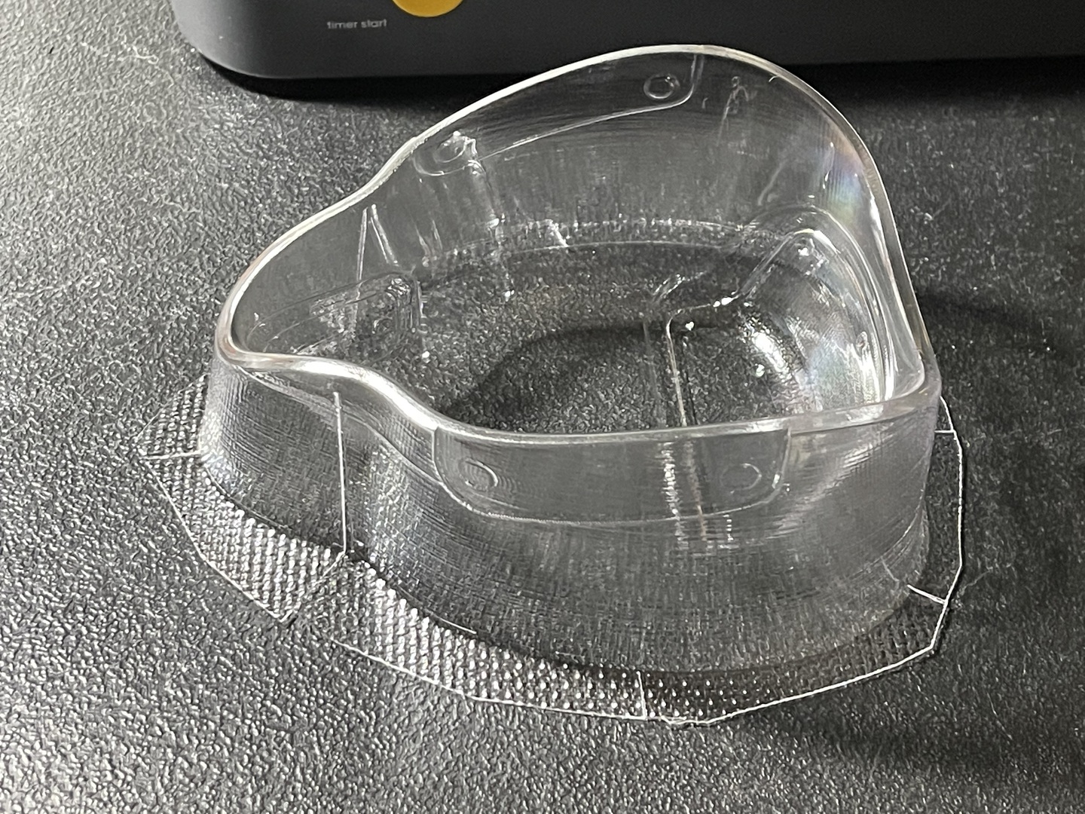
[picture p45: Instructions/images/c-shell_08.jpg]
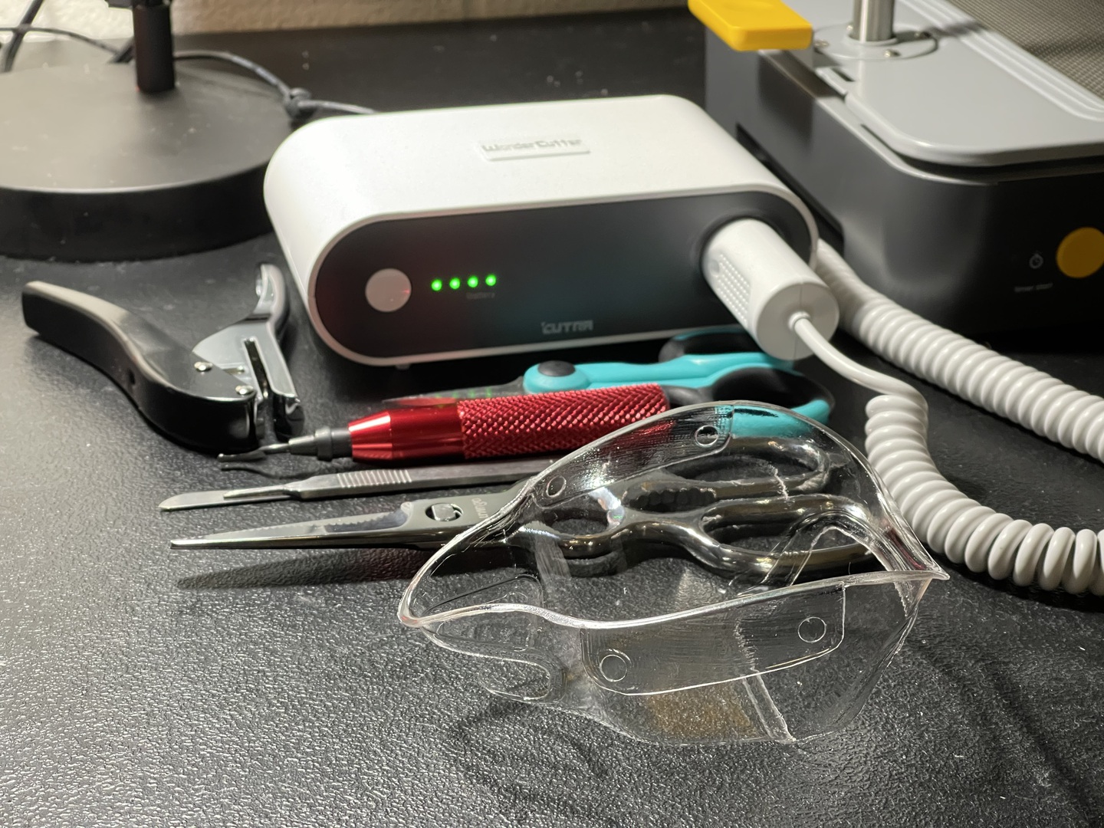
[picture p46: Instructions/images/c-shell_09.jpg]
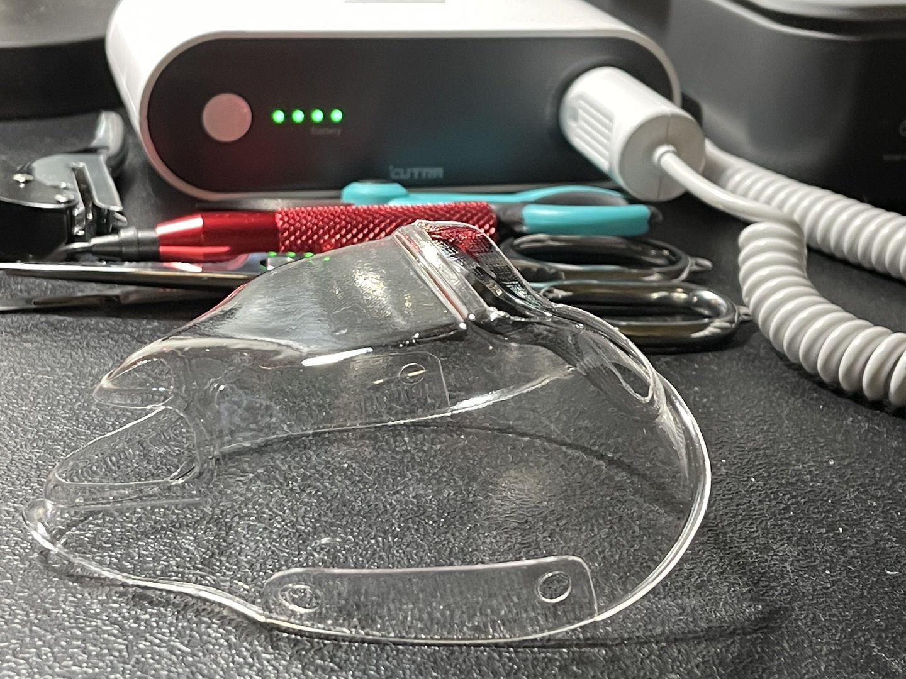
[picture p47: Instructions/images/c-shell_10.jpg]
   

# Glue the Mask Inserts into the Shell Openings

Using an industrial strength glue with a precision tip, like E6000 Jewelry & Bead (https://www.amazon.com/dp/B01C8EUUU0/ref=cm_sw_em_r_mt_dp_9FJJMGMW6XZNTZM1FEEE), the inserts should be glued into the mask shell openings, sealing the joints between the PETG clear shell and the 3D printed inserts. The goal is to have the inserts provide rigidity to the shell and to ensure that all the air goes through the round holes of the inserts that will be covered with filters.

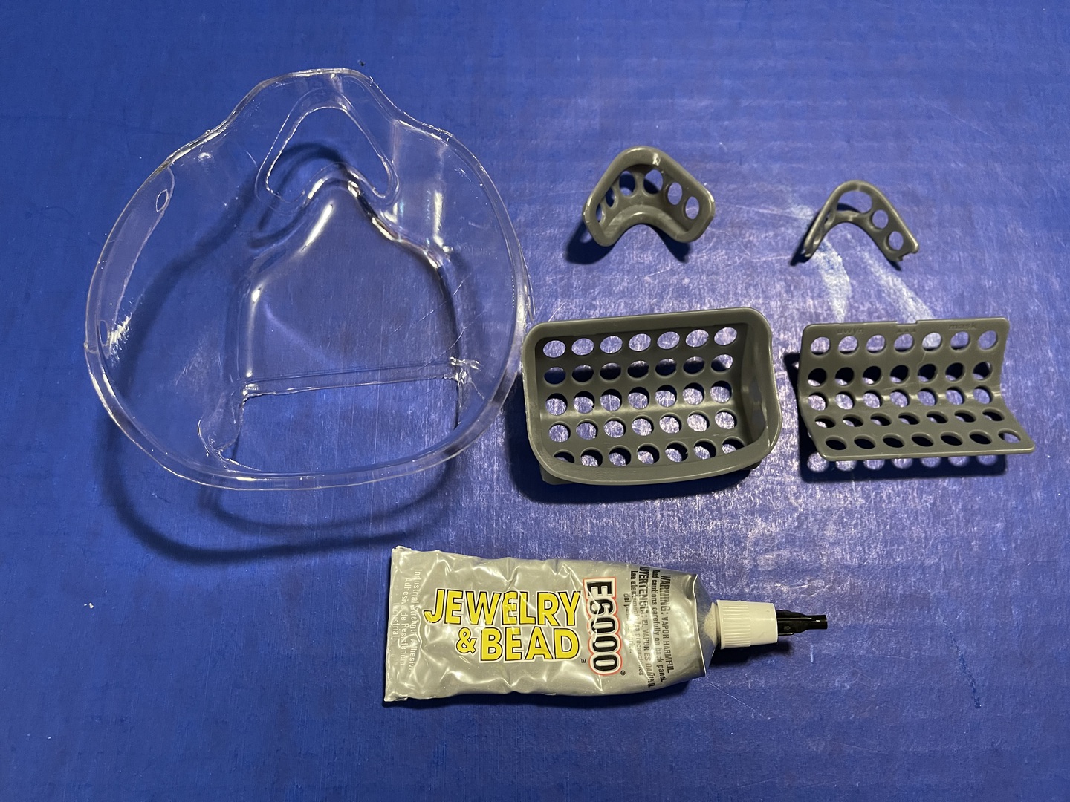
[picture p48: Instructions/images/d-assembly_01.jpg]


Start with the bottom insert, the largest one, and slowly and uniformly apply the glue all around the outside slab. By holding the center of the insert between your thumb and index finger, you should be able to cleanly apply the glue without getting it on other parts of the insert, nor your fingers.

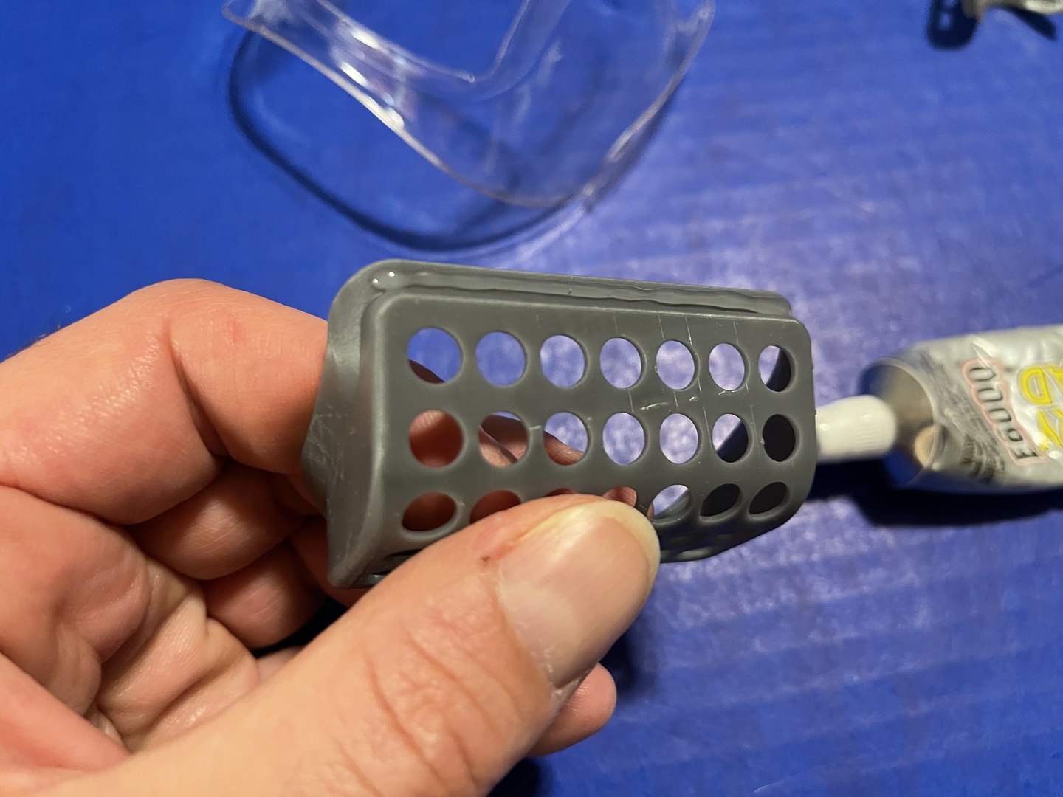
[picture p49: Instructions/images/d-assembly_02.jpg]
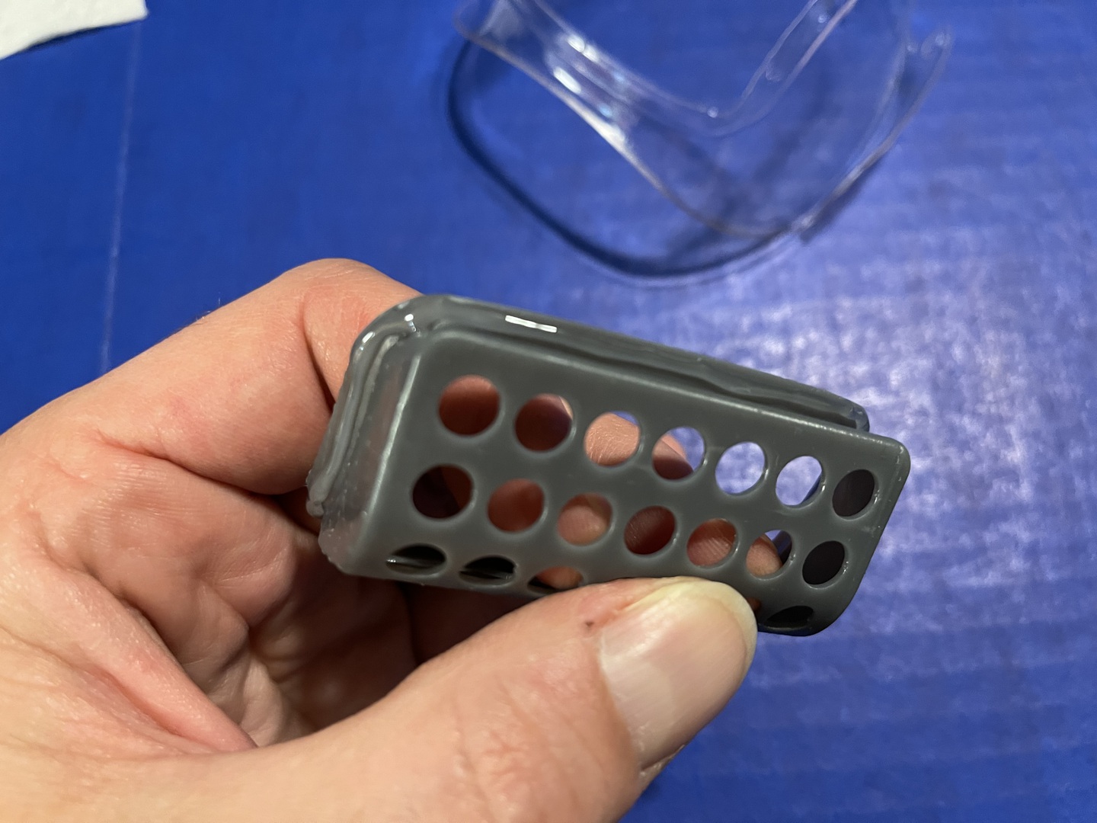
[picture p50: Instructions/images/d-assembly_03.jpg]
 

The next step requires more dexterity and precision, using one hand you'll hold the shell and with the other hand you'll pivot the insert into the shell from the bottom. Then, in one rotational movement, you'll push it further into the opening until the top snaps in place. Be very careful to not sway during this motion because you'll get glue on areas of the shell that should remain perfectly clear. Should that happen, most glues can be cleaned off with isopropyl alcohol and a microfiber cloth once they've slightly tried but not fully cured.

If you've cut the opening at the right size, this will mechanically hold the insert in place while the glue provides the seal and additional fixation. If you cut the hole too small, it might be impossible to push the insert through and the sides of the shell might curl up, preventing the glue from being uniformly squished. If you cut the hole too large, the insert will not mechanically hold in place and the mask will not be as sturdy as it could be.

Once the insert properly snaps in place, it will be almost impossible to get it back out without damaging the mask's shell. So if you want to practice before applying glue, be aware that you might have to sacrifice some shells.

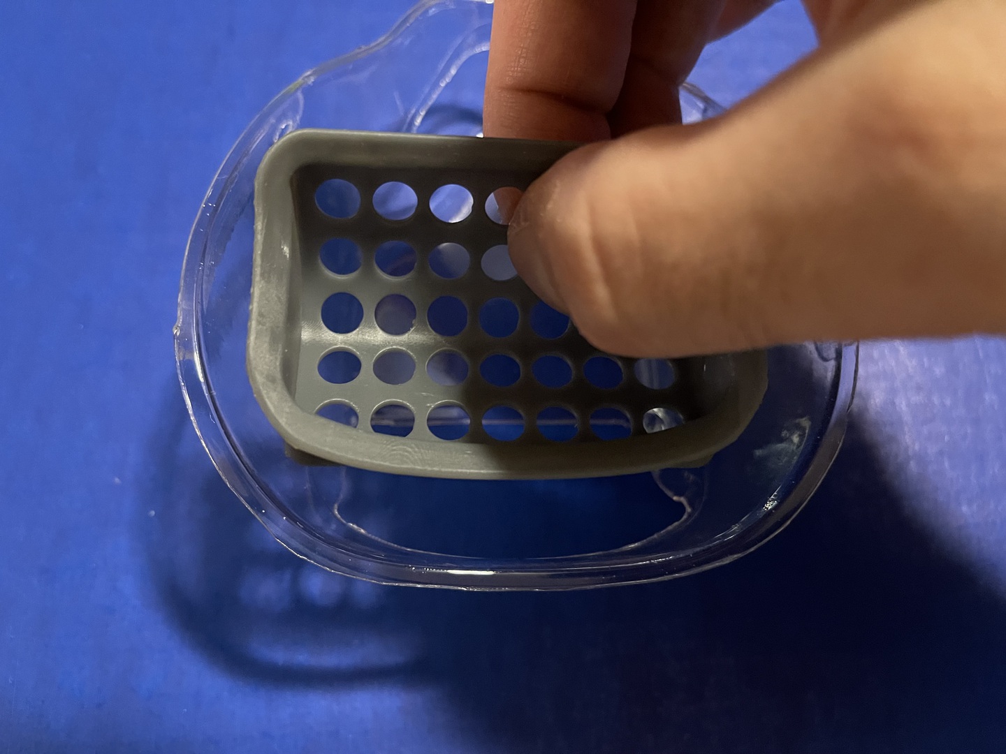
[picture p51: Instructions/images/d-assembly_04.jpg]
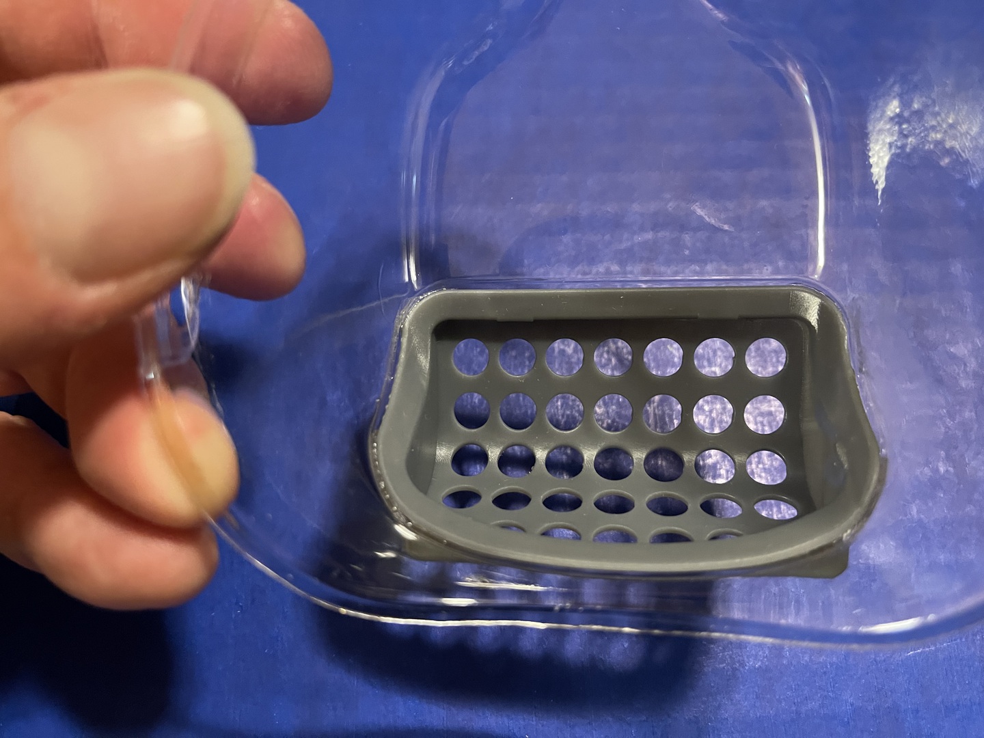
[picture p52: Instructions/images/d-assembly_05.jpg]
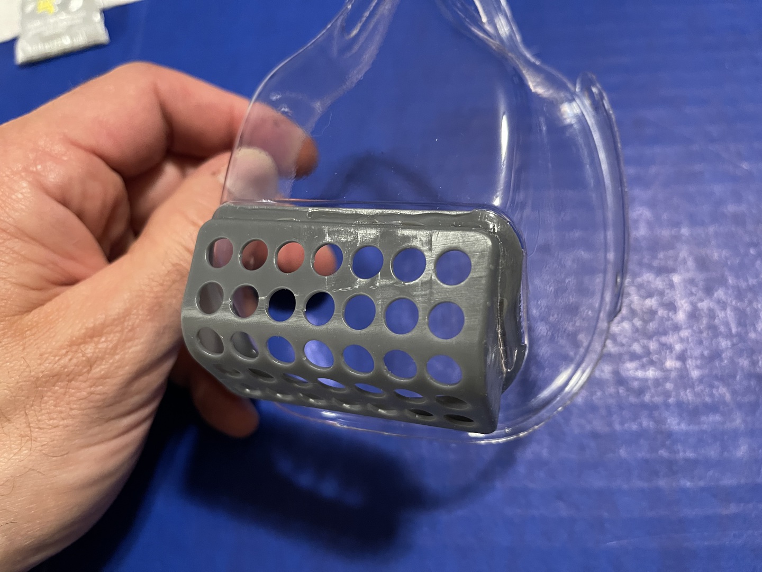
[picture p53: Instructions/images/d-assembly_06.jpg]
  

Next you'll do the same to the top insert. While holding it between your thumb and index finger, slowly and uniformly apply the glue all around the outside slab.

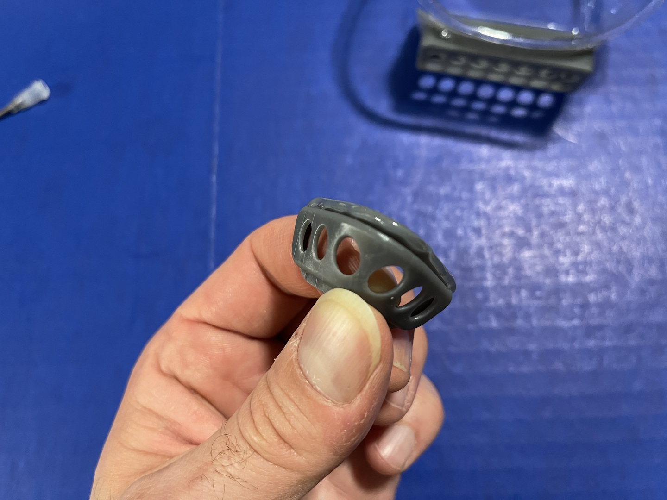
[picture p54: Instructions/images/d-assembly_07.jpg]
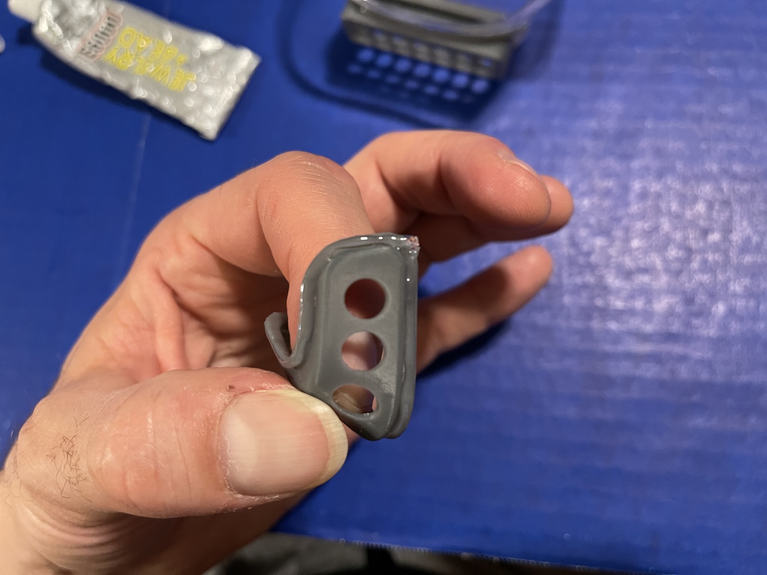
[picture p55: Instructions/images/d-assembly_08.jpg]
 

Attaching the top insert is similar to the bottom one. You'll once more hold the shell with one hand, and pivot one of the sides of the top insert into the shell. Again, in one motion you'll push the other side in, snapping the insert in place. I start with the left side and snap in the right. Given the small size of the top insert, it's easy to accidentally push the top edge through the shell opening while focusing on the sides. Just be aware of this while being careful, and it should work out fine.

All the same observations about the bottom opening's size apply to the top opening. If you cut the shell correctly and glued the top insert in place, the mask will become more rigid and the glue will provide a seal and additional fixation.

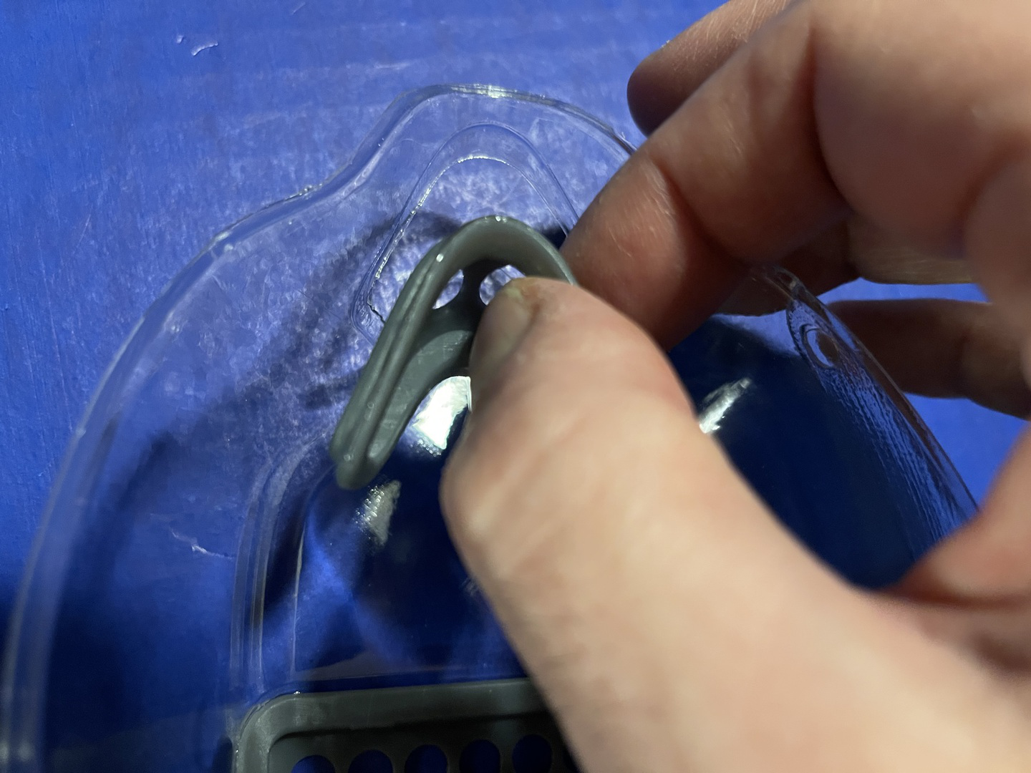
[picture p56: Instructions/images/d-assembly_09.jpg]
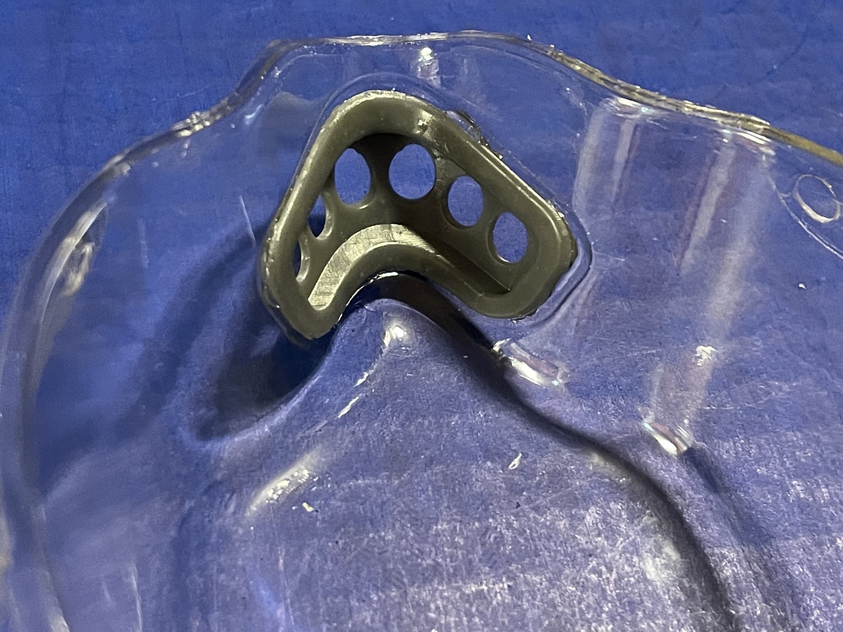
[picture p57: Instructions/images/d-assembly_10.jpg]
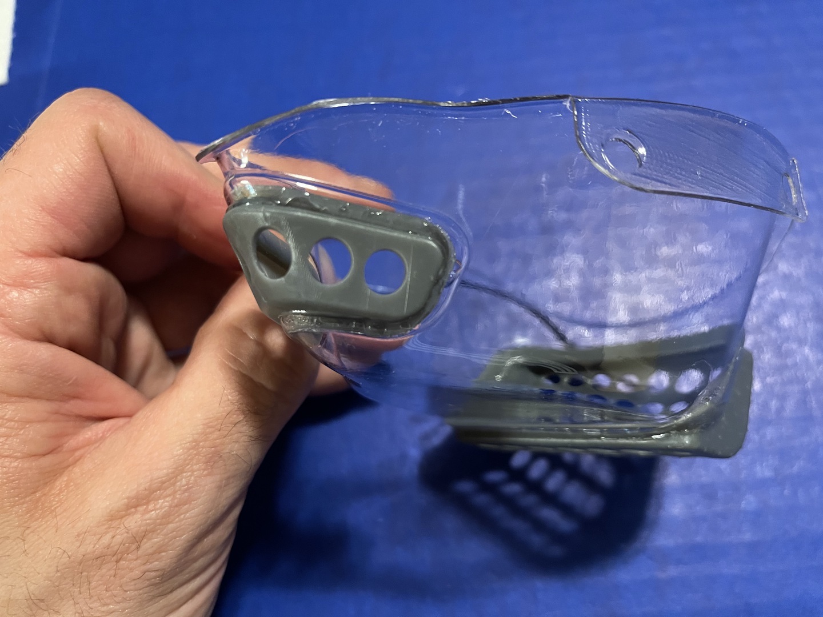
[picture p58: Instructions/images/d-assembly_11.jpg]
  

Once both inserts are glued, you should let the glue cure and off-gas for a while. I recommend at least 24 hours, preferably 48, at room temperature. This largely depends on the glue you used, so make sure you read the instructions.

# Glue the Seal to the Mask Shell

To apply the seal, I use a two step process. I first add a layer of thin neophrene foam on the flat area that presses against your face for comfort, and then I add thick weather seal rubber foam on the inside of the edges to ensure a great fit.

This neophrene foam works great and comes with a very strong pressure sensitive adhesive: Pres-On P8206RL00.50XOH Neoprene Foam Tape, 1/16" x 1/2" x 100', Black (https://www.amazon.com/dp/B01G382DX4/ref=cm_sw_em_r_mt_dp_7B6K2ZGGPDPRPZGKDAQ4). Work slowly and methodically when you apply it on the flat area of the edges, once the sticky side touches the shell it's virtually impossible to remove without ripping the foam.

I align the outside edge of the neophrene with the outside edge of the mask, and then slowly follow, fold inwards and press in small segments. When I make it all the way through, I try to cut it straight so that the extremities align without a gap. When done, I go over the whole edge again and firmly press on the foam to ensure that it sticks as well as possible.

   

For the second part of the seal, I use thick soft weather sealing foam that easily compresses and expands. This makes up for the differences between the mask's edge and the shape of your face. Frost King R338H Self-Stick Rubber Foam Weatherseal, 3/8"W, 3/16"T (https://www.amazon.com/dp/B000BQWWF4/ref=cm_sw_em_r_mt_dp_DVGWEH7WTNRTA7140WKV) works great, but the adhesive isn't strong enough for daily mask use, so I attach it with hot glue.

Using hot glue is a little bit more permissive than the adhesive on the neophrene foam, it allows you to reposition for a little while and get it perfectly aligned to the edge. I work in segments again, first applying a strip of glue and then pressing the rubber foam onto it. The top of the mask where your nose goes can get tricky, so I bend the rubber foam first before pushing it into that curve, this ensures that it goes all the way to the end without leaving a gap. When you reach the end, I cut the strip a few millimeters too long. This lets me perfectly match up the extremities. Finally, I also go over the whole edge again and once more firmly press on the foam and check its alignment.

If you need a hot glue gun and glue, these are the ones I use:

- PROkleber Hot Melt Glue Gun Kit Full Size 100 Watt with Carry Bag and 12 pcs Glue Sticks (https://www.amazon.com/dp/B071JMFSRJ/ref=cm_sw_em_r_mt_dp_H5DN96DFSHAFS12T28AX)
- Gorilla Hot Glue Sticks, Full Size, 8" Long x .43" Diameter, 20 Count, Clear (https://www.amazon.com/dp/B071HH42WW/ref=cm_sw_em_r_mt_dp_6VVCTTJWH8C7AQ3QC4NY)

   

The finished mask should look like the pictures below. There might be a lot of off-gassing from all the glue that you just used, so it's recommended to let the assembled shell dry for a few days.

 

# Apply the Anti-Fog Coating

Even though the air flow in this sealed mask is very good, breathing will inherently accumulate water vapor and cause condensation. This is even more an issue when the outside temperature is cold. In order to prevent this, it's possible to have the mask shell treated with a permanent anti-fog coating, but all the quotes I received for this were too expensive for small scale production.

As an alternative, I've been applying a temporary anti-fog coating every couple of days. The best I found was Rain-X 630046 Interior Glass Anti-Fog (https://www.amazon.com/dp/B00T9LR9FA/ref=cm_sw_em_r_mt_dp_NRAHT35X22KDYEDTRTPB). Applying this works best using a microfiber cloth and patting it on the inside of the shell, then letting it dry. Don't wipe or spread out this coating with the cloth, you'll instead remove it and not have any of the anti-fog benefits.

# Insert the Filter and the Grates

When the mask is fully dry from applying the anti-fog coating, cut out filter pieces using the 3D printed templates. Push the filters into the mask inserts, making sure to line up all the edges so that all the round holes are covered.

Recommended filter materials are:

- Filti: https://filti.com/product/filti-face-mask-material
- BioDefensor: https://biodefensor.com

With the filters in place, you can snap in the bottom grate by fully inserting the bottom edge first and pushing in the top edge. The top grate will easily snap in place from any side.

Most images below have the seal removed for clarity.

     

It's recommended to daily replace the filters when in constant use. For occasional use, weekly replacement is acceptable.

To replace the filters, remove the grates by using the tiny 3D printed grate pull 'crowbar' or by pushing through from the outside inwards with a pointy object. One end of the crowbar is intended for the bottom filter and the other for the top. Insert the appropriate end at an angle so that the little hook grabs onto the filter grate, then pivot the tool away while gently pushing towards the filter for leverage. This will grab behind the grate and push it outwards, away from the mask shell.

# You're Done!

Finally, cut out a single 48" piece of elastic band and guide it through the holes of the side flaps. With the mask on your face, pull one loop behind your head and tie both ends of the strap together in another loop. You should feel a little bit of compression of the seal around the mask's edges but it should still feel comfortable. When you're happy with the fit, you can cut off the excess elastic band.

 

# Get in touch

I'd love to hear about what you're doing with my mask design.

Please don't hesitate to reach out:

- Twitter: https://twitter.com/gbevin
- Instagram: https://www.instagram.com/gbevin
- LinkedIn: https://www.linkedin.com/in/gbevin
- Facebook: https://facebook.com/gbevin
- GitHub: https://github.com/gbevin
- Email: gbevin[remove] at uwyn dot com
- Website: http://uwyn.com

©2020-2021 Geert Bevin, Uwyn LLC (http://uwyn.com)

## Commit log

2021-08-09 Added STL files
    [extralarge_bottom_grate.stl, extralarge_bottom_insert.stl, extralarge_grate_pull.stl, extralarge_seal.stl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]
2021-08-09 Added images for assembly instructions

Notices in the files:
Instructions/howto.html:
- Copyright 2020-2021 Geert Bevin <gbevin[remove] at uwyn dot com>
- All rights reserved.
